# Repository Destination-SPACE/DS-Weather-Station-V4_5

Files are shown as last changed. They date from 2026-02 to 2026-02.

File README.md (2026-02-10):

<div align="center">
    
    <h1>Destination Weather Station v4.5.2</h1>
    <p>An Open Source Remote Sensing Platform for National Taiwan Normal University 🇹🇼</p>
</div>

## 🌟 About the Project
Destination Weather Station is the the latest version of remote sensing tools developed to teach students across Taiwan about climate science and remote sensing in partnership with National Taiwan Normal University.
## ⚙️ Hardware
All hardware files can be found [here](hardware/destinationWeatherStation_v4-5/)
## 💻 Software
All program files can be found [here](software)
## 🗂️ Documentation
Documentation for the weather station can be found [here](https://destination-space.github.io/DS-Weather-Station-V4_5/)
## Licenses
Each of the above sections are individually licensed. Terms and conditions apply within their respective folders.

**Documentation - [Apache License 2.0](docs/LICENSE)** <br>
**Hardware - [CERN-OHL-P](hardware/destinationWeatherStation_v4-5//LICENSE)** <br>
**Software - [The MIT License](software/LICENSE)**

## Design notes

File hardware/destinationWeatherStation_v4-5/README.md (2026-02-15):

# Destination Weather Station v4.5 Hardware
KiCad files for Destination Weather Station v4.5

## KiCanvas
View schematic and PCB files with [KiCanvas](https://kicanvas.org/?github=https%3A%2F%2Fgithub.com%2FDestination-SPACE%2FDS-Weather-Station-V4_5%2Ftree%2Fmain%2Fhardware%2FdestinationWeatherStation_v4-5)

## Directory
### [🧾 Bill of Materials](bom/bom.md)
### [📐 Gerbers](manufacturing/gerbers)
### [📰 Schematics](manufacturing/destinationWeatherStation_v4-5.pdf)

Licensed under [CERN-OHL-P](LICENSE)

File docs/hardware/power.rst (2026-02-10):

.. Copyright 2026 Destination SPACE Inc.
   Licensed under the Apache License, Version 2.0 (the "License");
   you may not use this file except in compliance with the License.
   You may obtain a copy of the License at

      http://www.apache.org/licenses/LICENSE-2.0

   Unless required by applicable law or agreed to in writing, software
   distributed under the License is distributed on an "AS IS" BASIS,
   WITHOUT WARRANTIES OR CONDITIONS OF ANY KIND, either express or implied.
   See the License for the specific language governing permissions and
   limitations under the License.

.. _power:

Power
=====

The power subsystem of the weather station was designed with reverse voltage protection in mind. Typically, if a battery is connected to a circuit backwards, it will not work, or worse, fry the entire system. This is why reverse current protection is often added to circuits to prevent such user error. This allows the user to not have to worry about the polarity of their LiPo battery. On the Destination Weather Station v4.5 we have taken this one step further, by not only having reverse voltage/polarity protection, but also correcting this polarity. This works using the same principal as an `AC rectifier <https://en.wikipedia.org/wiki/Rectifier>`_ circuit. This DC rectifier consists of two `N-Channel MOSFETs <https://en.wikipedia.org/wiki/NMOS_logic>`_ and two `P-Channel MOSFETs <https://en.wikipedia.org/wiki/PMOS_logic>`_. These MOSFETs combine to essentially create a rectifier circuit, which will only allow the correct polarity to pass through the FETs. A schematic of this circuit can be found below.



**Note:** There is no over-current protection, so make sure to not exceed 5V in.

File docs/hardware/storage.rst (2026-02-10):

.. Copyright 2026 Destination SPACE Inc.
   Licensed under the Apache License, Version 2.0 (the "License");
   you may not use this file except in compliance with the License.
   You may obtain a copy of the License at

      http://www.apache.org/licenses/LICENSE-2.0

   Unless required by applicable law or agreed to in writing, software
   distributed under the License is distributed on an "AS IS" BASIS,
   WITHOUT WARRANTIES OR CONDITIONS OF ANY KIND, either express or implied.
   See the License for the specific language governing permissions and
   limitations under the License.

.. _storage:

Storage
=======

The storage on the Destination Weather station is simply a microSD card slot to store recorded sensor data for further evalulation. There is also chip-detect functionality which allows the code to know if a card has been inserted or not.

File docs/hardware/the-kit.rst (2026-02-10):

.. Copyright 2026 Destination SPACE Inc.
   Licensed under the Apache License, Version 2.0 (the "License");
   you may not use this file except in compliance with the License.
   You may obtain a copy of the License at

      http://www.apache.org/licenses/LICENSE-2.0

   Unless required by applicable law or agreed to in writing, software
   distributed under the License is distributed on an "AS IS" BASIS,
   WITHOUT WARRANTIES OR CONDITIONS OF ANY KIND, either express or implied.
   See the License for the specific language governing permissions and
   limitations under the License.

.. _the-kit:

What is in the Kit?
===================

.. Insert kit image here

Kit Contents
------------
- Destination Weather Station v4.5.2
- Seeeduino XIAO RP2040 microcontroller w/ headers
- 128x64px OLED display w/ headers
- SPDT power switch
- AAA battery case
- 8GB micro-SD card
- USB-A to USB-C cable
- USB microSD card adapter

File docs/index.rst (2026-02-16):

.. Copyright 2026 Destination SPACE Inc.
   Licensed under the Apache License, Version 2.0 (the "License");
   you may not use this file except in compliance with the License.
   You may obtain a copy of the License at

      http://www.apache.org/licenses/LICENSE-2.0

   Unless required by applicable law or agreed to in writing, software
   distributed under the License is distributed on an "AS IS" BASIS,
   WITHOUT WARRANTIES OR CONDITIONS OF ANY KIND, either express or implied.
   See the License for the specific language governing permissions and
   limitations under the License.

Destination Weather Station v4.5
================================

An Open Source Remote Sensing Platform for National Taiwan Normal University

Contents
--------



.. toctree::
   :caption: Getting Started
   :maxdepth: 2

   hardware/the-kit
   hardware/assembly

.. toctree::
   :caption: Configuration
   :maxdepth: 2

   software/install-arduino-ide

.. toctree::
   :caption: Sensors
   :maxdepth: 2

   sensors/index
   sensors/bme280
   sensors/ens160
   sensors/ltr390
   sensors/scd40
   sensors/veml7700

.. toctree::
   :caption: Hardware
   :maxdepth: 2

   hardware/index
   faq/troubleshooting
   hardware/power
   hardware/storage
   hardware/hid

.. toctree::
   :caption: Software
   :maxdepth: 2

   software/index
   software/blink
   software/sensor-test
   software/demo
   software/full-code

.. toctree::
   :caption: Activities
   :maxdepth: 2

   activities/index
   activities/temperature
   activities/humidity
   activities/CO2
   activities/VOCs
   activities/ALS
   activities/UVA

.. toctree::
   :caption: Manufacturing and Ordering Kits
   :maxdepth: 1

   manufacturing/index
   manufacturing/pcbs
   manufacturing/adafruit_sensors
   manufacturing/3d_printing
   manufacturing/building_kits

.. toctree::
   :caption: Miscellaneous
   :maxdepth: 2

   FAQ <faq/index>

.. * :ref:`genindex`
.. * :ref:`modindex`
.. * :ref:`search`

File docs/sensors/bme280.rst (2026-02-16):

.. Copyright 2026 Destination SPACE Inc.
   Licensed under the Apache License, Version 2.0 (the "License");
   you may not use this file except in compliance with the License.
   You may obtain a copy of the License at

      http://www.apache.org/licenses/LICENSE-2.0

   Unless required by applicable law or agreed to in writing, software
   distributed under the License is distributed on an "AS IS" BASIS,
   WITHOUT WARRANTIES OR CONDITIONS OF ANY KIND, either express or implied.
   See the License for the specific language governing permissions and
   limitations under the License.

.. _bme280:

BME280
======



The BME280 combined humidity and pressure sensor is a classic device used for accurately measuring temperature, pressure, and humidity.

Humidity
~~~~~~~~

.. list-table::
   :header-rows: 1

   * - Parameter
     - Specifications

   * - Operating Range
     - 0 - 100 %RH
   
   * - Absolute Accuracy
     - ±3 %RH
   
   * - Hysteresis
     - ± %RH



Pressure
~~~~~~~~

.. list-table::
   :header-rows: 1

   * - Parameter
     - Specifications

   * - Operating Range
     - 0 - 1100 hPa

   * - Absolute Accuracy
     - ± 1.0 hPa

   * - Relative Accuracy (700 - 900 hPa & 25 - 40 °C)
     - ± 0.12 hPa

Temperature
~~~~~~~~~~~

.. list-table::
   :header-rows: 1

   * - Parameter
     - Specifications

   * - Operating Range
     - 0 - 65 °C
   
   * - Absolute Accuracy
     - 0.5 °C

Functional Block Diagram
~~~~~~~~~~~~~~~~~~~~~~~~
Below is a functional block diagram for how the BME280 sensor works. The data for each parameter (humidity, pressure, and temperature) are measured using an analog sensor. The data is then converted from an analog voltage signal to a digital data signal. This data is then passed to the logic side of the sensor which sends and receives data to/from the host device.



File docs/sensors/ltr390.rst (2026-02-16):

.. Copyright 2026 Destination SPACE Inc.
   Licensed under the Apache License, Version 2.0 (the "License");
   you may not use this file except in compliance with the License.
   You may obtain a copy of the License at

      http://www.apache.org/licenses/LICENSE-2.0

   Unless required by applicable law or agreed to in writing, software
   distributed under the License is distributed on an "AS IS" BASIS,
   WITHOUT WARRANTIES OR CONDITIONS OF ANY KIND, either express or implied.
   See the License for the specific language governing permissions and
   limitations under the License.

.. _ltr390:

LTR390
======



The LTR390 optical sensor is a combined digital ambient light (ALS) and UVA sensor.

Ambient Light Specifications
~~~~~~~~~~~~~~~~~~~~~~~~~~~~

.. list-table::
   :header-rows: 1

   * - Parameter
     - Minimum
     - Typical
     - Maximum
     - Units
     - Condition
   
   * - ALS Output Resolution
     - 13
     - 18
     - 20
     - Bit
     - Programmable for 13, 16, 17, 18, 19, 20 bit
   
   * - Dark Level Count
     - -
     - 0
     - 5
     - count
     - 0 Lux, T_ope=25°C, 18-bit range

   * - Calibrated Lux Error In Gain Range 3
     - -10
     - -
     - 10
     - %
     - While LED, 5000K, T_ope=25°C

   * - ALS Accuracy
     - -25
     - -
     - 25
     - %
     - Across different light sources

UVS Specifications
~~~~~~~~~~~~~~~~~~

.. list-table::
   :header-rows: 1

   * - Parameter
     - Minimum
     - Typical
     - Maximum
     - Unit
     - Condition

   * - UVS Output Resolution
     - 13
     - 18
     - 20
     - Bit
     - Programmable for 13, 16,17, 18, 19, 20 bit
   
   * - UV Count
     - -
     - 160
     - -
     - count
     - UV LED 310nm, T_ope=25°C, 18-bit, Gain range = 18, Irradiance = 70uW/cm2

   * - UV Sensitivity
     - -
     - 2300
     - -
     - Counts/UVI
     - Gain range = 18, 20-bit

   * - UVI Accuracy (UVI>5)
     - -20
     - -
     - 20
     - %
     - Gain Range = 18, 20bit

   * - UVI Accuracy (UVI<5)
     - -1
     - -
     - 1
     - %
     - Gain Range = 18, 20bit

ALS Sensor
~~~~~~~~~~

The ambient light sensor is sensitive to a range of 450nm - 650nm and is centered at 535nm as seen in the graph below.



Additionally, below is a graph showing the angle of incidence of the sensor, where a normalized count of 1 indicates full sensitivity.



UVS Sensor
~~~~~~~~~~

The UVS sensor peaks in sensitive for UVA wavelengths (315-400) with some moderate sensitivity to low-energy UVB wavelengths. The graph below indicates the the response of the UVS sensor, which has a range of 275nm - 400nm and is centered at 320nm.



The Ultra-Violet Spectrum
~~~~~~~~~~~~~~~~~~~~~~~~~
The ultra-violet spectrum ranges from 10nm to 400nm. This is further subdivided into different bands of intensity, which are used in remote sensing and to indicate their danger.



UVA
~~~

UVA is the longest wavelength of the UV spectrum, ranging from 400nm to 315nm. UVA is the primary cause of sunburns encountered from being in the sun too long. This is because the longer wavelength allows it to penetrate deeper into the skin.

UVB
~~~

UVB is a the middle band of the UV spectrum and ranges from 315nm to 280nm. UVB is mostly absorbed by the ozone layer, but can still reach the earth's surface. This is primarily seen at higher latitudes and elevations. Because UVB has a shorter wavelength, this is the primary cause of skin cancer and blistering from sunburns.

UVC
~~~

UVB is the highest energy band in the UV spectrum, ranging from 280nm to 100nm. UVC is entirely filtered out by the Earth's atmosphere, so is no danger to life on the surface, but can become a risk during air travel or in space. UVC is a type of ionizing radiation, meaning it easily kills cells. This is useful for UV disinfection lights.

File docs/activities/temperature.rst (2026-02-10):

.. Copyright 2026 Destination SPACE Inc.
   Licensed under the Apache License, Version 2.0 (the "License");
   you may not use this file except in compliance with the License.
   You may obtain a copy of the License at

      http://www.apache.org/licenses/LICENSE-2.0

   Unless required by applicable law or agreed to in writing, software
   distributed under the License is distributed on an "AS IS" BASIS,
   WITHOUT WARRANTIES OR CONDITIONS OF ANY KIND, either express or implied.
   See the License for the specific language governing permissions and
   limitations under the License.

.. _temperature:

Temperature Activity - Microclimates
====================================

Duration: 15 minutes

Background
----------

Materials
---------

- Destination Weather Station
- Paper
- Pencil

Procedure
---------

1. Make a map of the classroom on a sheet of paper. Make sure to label any windows, doors, air vents, and significant heat sources.
2. Make a prediction for which areas of the classroom you think will be hot or cold.
3. On your map, mark locations in the classroom you want to collect data.
4. Using your weather station, record the average temperature at each location you marked on your map.

Discussion Questions
--------------------

1. Did your predictions match the data you collected? Why might they be different?
2. What do you think caused that part of the classroom to be that temperature?

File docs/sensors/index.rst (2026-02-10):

.. Copyright 2026 Destination SPACE Inc.
   Licensed under the Apache License, Version 2.0 (the "License");
   you may not use this file except in compliance with the License.
   You may obtain a copy of the License at

      http://www.apache.org/licenses/LICENSE-2.0

   Unless required by applicable law or agreed to in writing, software
   distributed under the License is distributed on an "AS IS" BASIS,
   WITHOUT WARRANTIES OR CONDITIONS OF ANY KIND, either express or implied.
   See the License for the specific language governing permissions and
   limitations under the License.

.. _sensors:

Overview of Sensors
===================

The Destination Weather Station is equipped with a :ref:`Bosch BME280 combined humidity and pressure sensor<bme280>`.

In the expansion sensor kit, several more environmental sensors are provided to measure a wide variety of parameters. These include:

* :ref:`ScioSense ENS160 - Digital metal-oxide multi-gas sensor<ens160>`
* :ref:`Lite-On LTR390 - Ambient light and ultravoiolet light sensor<ltr390>`
* :ref:`Sensirion SCD40 - Miniature CO2 sensor<SCD40>`
* :ref:`Vishay VEML7700 - High accuracy ambient light sensor<veml7700>`

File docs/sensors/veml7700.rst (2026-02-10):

.. Copyright 2026 Destination SPACE Inc.
   Licensed under the Apache License, Version 2.0 (the "License");
   you may not use this file except in compliance with the License.
   You may obtain a copy of the License at

      http://www.apache.org/licenses/LICENSE-2.0

   Unless required by applicable law or agreed to in writing, software
   distributed under the License is distributed on an "AS IS" BASIS,
   WITHOUT WARRANTIES OR CONDITIONS OF ANY KIND, either express or implied.
   See the License for the specific language governing permissions and
   limitations under the License.

.. _veml7700:

VEML7700
========



The VEML7700 high accuracy 16-bit light sensor can be used to precisely measure ambient light. Below is a functional block diagram of the device, where the sensor is an ALS photodiode.



Specifications
~~~~~~~~~~~~~~

.. list-table::
   :header-rows: 1

   * - Parameter
     - Typical Value
     - Units
   
   * - Digital resolution
     - 0.0036
     - lux/bit
   
   * - Detectable minimum illuminance
     - 0.0072
     - lux
   
   * - Detectable maximum illuminance
     - 120,000
     - lux
   
   * - Dark offset
     - 3
     - steps

Below is a graph showing the spectral response of the sensor. It is sensitive to wavelengths ranging from 450nm - 650nm, normalized at 550nm.



Additionally, below is a graph showing the sensitivity of the white light channel on the sensor.



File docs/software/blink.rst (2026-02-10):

.. Copyright 2026 Destination SPACE Inc.
   Licensed under the Apache License, Version 2.0 (the "License");
   you may not use this file except in compliance with the License.
   You may obtain a copy of the License at

      http://www.apache.org/licenses/LICENSE-2.0

   Unless required by applicable law or agreed to in writing, software
   distributed under the License is distributed on an "AS IS" BASIS,
   WITHOUT WARRANTIES OR CONDITIONS OF ANY KIND, either express or implied.
   See the License for the specific language governing permissions and
   limitations under the License.

.. _blink-sketch:

Blink Sketch
============

The `Blink <https://github.com/Destination-SPACE/DS-Weather-Station-V4_5/blob/main/software/Blink/Blink.ino>`_ sketch is used as a beginners program and to test the on-board RGB LED and NeoPixel.

Libraries
---------

The Blink Sketch has only one required library. This library is the `Adafruit NeoPixel Library <https://github.com/adafruit/Adafruit_NeoPixel>`_. This is used to send commands to the NeoPixel RGB LED on the Seeeduino XIAO.

.. code-block:: cpp
   
   #include <Adafruit_NeoPixel.h>

Hardware Definitions
--------------------

Several hardware definitions need to be defined to use the RBG LED and the NeoPixel. These are defined by assigning each variable a General Purpose Input-Output (GPIO) pin on the XIAO and any other criteria specified by the NeoPixel library. What these definitions do is define the red, green, and blue pins of the normal RGB LED a GPIO pin, define the power and signal pin for the NeoPixel, and define the number of NeoPixels on the board.

.. code-block:: cpp

   #define RGB_R 17
   #define RGB_G 16
   #define RGB_B 25
   #define NEOPIXEL_PWR 11
   #define NEOPIXEL_PIN 12
   #define NEOPIXEL_NUM 1

Following the hardware definitions, the information specified above needs to be defined in the NeoPixel definition function

.. code-block:: cpp

   Adafruit_NeoPixel pixels(NEOPIXEL_NUM, NEOPIXEL_PIN, NEO_GRB + NEO_KHZ800);

Setup Function
--------------

The next step is to initialize the LEDs for the primary loop function. This is done by starting the NeoPixel function, initializing the power and signal pins, and defining the RGB LEDs pins as outputs.

.. code-block:: cpp

   void setup() {
      //Initialize NeoPixel
      pixels.begin();
      pinMode(NEOPIXEL_PWR, OUTPUT);
      digitalWrite(NEOPIXEL_PWR, HIGH);

      //Initialize RGB LED
      pinMode(RGB_R, OUTPUT);
      pinMode(RGB_G, OUTPUT);
      pinMode(RGB_B, OUTPUT);
   }

Loop Function
-------------

The final step is to send the commands to the NeoPixel and RGB LED. This is done by first clearing the NeoPixel's stored data, defining the color, and sending the neopixel the data. Additionally, there is a custom function to easily control the color of the RGB LED. This works by passing the red, green, and blue values to the function ``setColor()``. An example of the NeoPixel code and the RGB LED can be found below

.. code-block:: cpp
   
   pixels.clear();
   pixels.setPixelColor(0, pixels.Color(15, 25, 205));
   delay(400); // How long the NeoPixel stays on
   pixels.show();

.. code-block:: cpp
   
   setColor(15, 25, 205);

   void setColor(int VAL_GRN, int VAL_RED, int VAL_BLU){
      analogWrite(RGB_R, 255 - VAL_RED);
      analogWrite(RGB_G, 255 - VAL_GRN);
      analogWrite(RGB_B, 255 - VAL_BLU);
   }

Full Code
--------- 

Below is the full Blink example sketch

.. code-block:: cpp
   
   #include <Adafruit_NeoPixel.h> // Import Adafruit NeoPixel library

   //Define Hardware
   #define RGB_R 17
   #define RGB_G 16
   #define RGB_B 25
   #define NEOPIXEL_PWR 11
   #define NEOPIXEL_PIN 12
   #define NEOPIXEL_NUM 1

   Adafruit_NeoPixel pixels(NEOPIXEL_NUM, NEOPIXEL_PIN, NEO_GRB + NEO_KHZ800); // Define NeoPixel

   void setup() {
      //Initialize NeoPixel
      pixels.begin();
      pinMode(NEOPIXEL_PWR, OUTPUT);
      digitalWrite(NEOPIXEL_PWR, HIGH);

      //Initialize RGB LED
      pinMode(RGB_R, OUTPUT);
      pinMode(RGB_G, OUTPUT);
      pinMode(RGB_B, OUTPUT);
   }

   void loop() { 
      pixels.clear();
      pixels.setPixelColor(0, pixels.Color(15, 25, 205));
      setColor(15, 25, 205);
      delay(400);

      pixels.show();
      pixels.clear();
      pixels.setPixelColor(0, pixels.Color(103, 25, 205));
      setColor(15, 25, 205);
      delay(400);

      pixels.show();
      pixels.clear();
      pixels.setPixelColor(0, pixels.Color(233, 242, 205));
      setColor(233, 242, 205);
      delay(400);

      pixels.show();
      pixels.clear();
      pixels.setPixelColor(0, pixels.Color(233, 23, 23));
      setColor(233, 23, 23);
      delay(400);

      pixels.show();
      pixels.clear();
      pixels.setPixelColor(0, pixels.Color(12, 66, 101));
      setColor(12, 66, 101);
      delay(400);

      pixels.show();
      delay(500);
   }

   //Function to change color of RGB LED
   void setColor(int VAL_GRN, int VAL_RED, int VAL_BLU){
      analogWrite(RGB_R, 255 - VAL_RED);
      analogWrite(RGB_G, 255 - VAL_GRN);
      analogWrite(RGB_B, 255 - VAL_BLU);
   }

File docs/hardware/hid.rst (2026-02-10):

.. Copyright 2026 Destination SPACE Inc.
   Licensed under the Apache License, Version 2.0 (the "License");
   you may not use this file except in compliance with the License.
   You may obtain a copy of the License at

      http://www.apache.org/licenses/LICENSE-2.0

   Unless required by applicable law or agreed to in writing, software
   distributed under the License is distributed on an "AS IS" BASIS,
   WITHOUT WARRANTIES OR CONDITIONS OF ANY KIND, either express or implied.
   See the License for the specific language governing permissions and
   limitations under the License.

.. _hid:

Human Interface Devices
=======================

On the Destination Weather Station there are 4 buttons, which are the primary way to interact with the device. These buttons are each labeled with arrows ↑, ↓, ←, →. These buttons are used to scroll through the menus and to switch between the different data displays.

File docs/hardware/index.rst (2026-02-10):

.. Copyright 2026 Destination SPACE Inc.
   Licensed under the Apache License, Version 2.0 (the "License");
   you may not use this file except in compliance with the License.
   You may obtain a copy of the License at

      http://www.apache.org/licenses/LICENSE-2.0

   Unless required by applicable law or agreed to in writing, software
   distributed under the License is distributed on an "AS IS" BASIS,
   WITHOUT WARRANTIES OR CONDITIONS OF ANY KIND, either express or implied.
   See the License for the specific language governing permissions and
   limitations under the License.

.. _hardware:

Overview of Hardware
====================

The Destination Weather Station was designed in `KiCad <https://www.kicad.org/>`_ and assembled by hand. the weather station includes several features that improve user experience. These are:

.. toctree::
   :maxdepth: 1

   power
   storage
   hid

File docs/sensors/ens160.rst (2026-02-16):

.. Copyright 2026 Destination SPACE Inc.
   Licensed under the Apache License, Version 2.0 (the "License");
   you may not use this file except in compliance with the License.
   You may obtain a copy of the License at

      http://www.apache.org/licenses/LICENSE-2.0

   Unless required by applicable law or agreed to in writing, software
   distributed under the License is distributed on an "AS IS" BASIS,
   WITHOUT WARRANTIES OR CONDITIONS OF ANY KIND, either express or implied.
   See the License for the specific language governing permissions and
   limitations under the License.

.. _ens160:

ENS160
======



The ENS160 digital metal-oxide multi-gas sensor measures volatile organic compounds (VOCs), which can be used to measure total VOC content (TVOC), air quality index (AQI), and calculate an approximate value for carbon-dioxide concentration (eCO2).

Specifications
~~~~~~~~~~~~~~

.. list-table::
   :header-rows: 1

   * - Parameter
     - Range
     - Resolution
     - Units

   * - TVOC
     - 0 - 65,000
     - 1
     - ppb

   * - eCO2
     - 400 - 65,000
     - 1
     - ppm CO2 equivalent

   * - AQI-UBA
     - 1 to 5
     - 1
     - -

   * - AQI-EPA
     - 0 - 500
     - 1
     - -

TVOC
~~~~
Total Volatile Organic Compounds (TVOC) is a useful parameter used to determine the quality of the air in a given area. This is incredibly important for urban environments and in indoor settings. This is typically measured in parts-per-billion (ppb), but in polluted environments, can reach into the parts-per-million (ppm) range.

eCO2
~~~~
The ENS160 sensor uses an algorithm to calculate an approximate value for carbon-dioxide (CO2) concentration. While the sensor cannot directly measure CO2, it's algorithm can closely approximate this value, as seen in the graph below.



In the graph, the calculated eCO2 measurement is being compared to a non-dispersive infrared CO2 sensor. It can closely approximate the CO2 concentration, but it is not perfect.

In the graphs below, ScioSense has provided eCO2 measurement for different environments, such as in a bedroom, kitchen, and bathroom. These graphs show that different conditions, such as closing a window, cooking, or being in a room can increase CO2 concentrations.







AQI
~~~
Air Quality Index (AQI) is the typical parameter used to judge the quality of air and how polluted it is. There are several different scales used to measure this value, but they are all based on the concentration of VOCs. For example, the United States uses the `NowCast <https://www.airnow.gov/aqi/aqi-basics/>`_ algorithm developed by the Environmental Protection Agency (EPA) ranging from 0 to 500, the European Union's `European Environment Agency <https://airindex.eea.europa.eu/AQI/index.html>`_ (EEA) uses a scale ranging from 0 to 1250, and Taiwan's `Ministry of Environment <https://airtw.epa.gov.tw/ENG/Information/Standard/AirQualityIndicator.aspx>`_ uses a similar scale to the United States, ranging from 0 to 500. The figures below show each of these indexes.

Environmental Protection Agency (EPA)



European Environment Agency (EEA)



Ministry of Environment



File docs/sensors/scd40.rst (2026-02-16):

.. Copyright 2026 Destination SPACE Inc.
   Licensed under the Apache License, Version 2.0 (the "License");
   you may not use this file except in compliance with the License.
   You may obtain a copy of the License at

      http://www.apache.org/licenses/LICENSE-2.0

   Unless required by applicable law or agreed to in writing, software
   distributed under the License is distributed on an "AS IS" BASIS,
   WITHOUT WARRANTIES OR CONDITIONS OF ANY KIND, either express or implied.
   See the License for the specific language governing permissions and
   limitations under the License.

.. _scd40:

SCD40
=====



THe SCD40 CO2 sensor uses photoacoustic non-dispersive infrared (NDIR) technology to measure actual CO2 concentration, unlike the eCO2 measurement on the :ref:`ENS160<ens160>`. This works by measuring the attenuation of an infrared light shining through the gas onto an acoustic transducer. Along with the sample chamber there is a reference nitrogen sample used to compare the CO2 measurement to the known gas. This process works according to Beer-Lambert law which is this attenuation of the gas.



CO2 Sensing Performance
~~~~~~~~~~~~~~~~~~~~~~~

.. list-table::
   :header-rows: 1

   * - Parameter
     - Conditions
     - Value
   
   * - Output range
     - -
     - 0 - 40,000ppm
   
   * - Accuracy
     - 400ppm - 2,000ppm
     - ±(50ppm + 5% of reading)
   
   * - Repeatability
     - Typical
     - ±10ppm

Humidity Sensing Performance
~~~~~~~~~~~~~~~~~~~~~~~~~~~~

.. list-table::
   :header-rows: 1

   * - Parameter
     - Conditions
     - Value
   
   * - Range
     - -
     - 0 %RH - 100 %RH

   * - Accuracy
     - 15°C - 35°C, 20 %RH - 65 %RH
     - ±6 %RH

   * - Accuracy
     - -10°C - 60°C, 0 %RH - 100 %RH
     - ±9 %RH

   * - Repeatability
     - Typical
     - ±0.4 %RH

Temperature Sensing Performance
~~~~~~~~~~~~~~~~~~~~~~~~~~~~~~~

.. list-table::
   :header-rows: 1

   * - Parameter
     - Conditions
     - Value
   
   * - Range
     - -
     - -10°C - 60°C
   
   * - Accuracy
     - 15°C - 35°C
     - ±0.8°C
   
   * - Accuracy
     - -10°C - 60°C
     - ±1.5°C

   * - Repeatability
     - Typical
     - ±0.1°C

Measuring CO2
~~~~~~~~~~~~~

Measuring CO2 is another important parameter for indoor and outdoor air quality. Health Canada recommends not exceeding 1000ppm of CO2 in a 24 hour period. A high concentration of CO2 can increase the risk of respiratory symptoms, decreased cognitive function, and neurophysiological symptoms such as headaches, tiredness, and dizziness. The graph below shows different concentrations and what effects one may encounter at that concentration.



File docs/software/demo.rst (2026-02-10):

.. Copyright 2026 Destination SPACE Inc.
   Licensed under the Apache License, Version 2.0 (the "License");
   you may not use this file except in compliance with the License.
   You may obtain a copy of the License at

      http://www.apache.org/licenses/LICENSE-2.0

   Unless required by applicable law or agreed to in writing, software
   distributed under the License is distributed on an "AS IS" BASIS,
   WITHOUT WARRANTIES OR CONDITIONS OF ANY KIND, either express or implied.
   See the License for the specific language governing permissions and
   limitations under the License.

.. _demo-sketch:

Demo Sketch
===========

The `Demo <https://github.com/Destination-SPACE/DS-Weather-Station-V4_5/blob/main/software/Demo/Demo.ino>`_ sketch is used as an introductory program to most of the features on the weather station. This includes scrollable menus for all sensors.

There is no data recording in this example.

Button Menu
-----------

On the weather station there are 4 buttons, ↑, ↓, ←, →.

The ← and → buttons are used to scroll between the weather menu, air quality menu, and the light menu.

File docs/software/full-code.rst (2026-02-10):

.. Copyright 2026 Destination SPACE Inc.
   Licensed under the Apache License, Version 2.0 (the "License");
   you may not use this file except in compliance with the License.
   You may obtain a copy of the License at

      http://www.apache.org/licenses/LICENSE-2.0

   Unless required by applicable law or agreed to in writing, software
   distributed under the License is distributed on an "AS IS" BASIS,
   WITHOUT WARRANTIES OR CONDITIONS OF ANY KIND, either express or implied.
   See the License for the specific language governing permissions and
   limitations under the License.

.. _blink:

Full Code Sketch
================

The `Full Code <https://github.com/Destination-SPACE/DS-Weather-Station-V4_5/blob/main/software/Full_Code/Full_Code.ino>`_ sketch incorporates all of the components of the weather station, including data recording. This has all the menus of the `Demo <https://github.com/Destination-SPACE/DS-Weather-Station-V4_5/blob/main/software/Demo/Demo.ino>`_ sketch as well as a menu used to start and stop data recording.

Program Overview
----------------

Button Menu
-----------

On the weather station there are 4 buttons, ↑, ↓, ←, →.

The ← and → buttons are used to scroll between the weather menu, air quality menu, and the light menu.

The ↑ arrow is used to navigate to the data recording menu. Here you can choose to either start recording data or pause data recording. **data recording is paused by default**. Press the → button to confirm your selection.

The ↓ is used to navigate the data recording menu above. When in either the air quality or light menu, pressing it will return you to the weather menu.

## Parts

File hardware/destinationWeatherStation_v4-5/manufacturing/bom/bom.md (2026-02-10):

# Bill of Materials
*Note: Some parts may be replaced with suitable alternatives

| Item | Qty | Reference | Value | Datasheet | Manufacturer | Manufacturer Part Number | Package |
|-----:|----:|:---------:|:-----:|:----------|:-------------|:-------------------------|--------:|
| 1 | 1 | C1 | 10uF | [AVX-CX5R-KGM](../datasheets/AVX-CX5R-KGM-MLCC.pdf) | KYOCERA AVX | KGM15CR51A106MT | 0603 |
| 2 | 3 | C2, C3, C4 | 0.1uF | [AVX-CX5R-KGM](../datasheets/AVX-CX5R-KGM-MLCC.pdf) | KYOCERA AVX | KGM15AR51H104KT | 0603 | 
| 3 | 10 | R1, R2, R3, R4, R5, R6, R7, R8, R9, R10 | 10K | [D/CRCW e3](../datasheets/Vishay-Dale-DCRCWe3.pdf) | Vishay Dale | CRCW060310K0JNEB | 0603 |
| 3 | 2 | R11, R12 | 0R | [D/CRCW e3](../datasheets/Vishay-Dale-DCRCWe3.pdf) | Vishay Dale | CRCW06030000Z0EA | 0603 |
| 4 | 2 | Q1, Q2 | IRLML6244TRPBF | [IRLML6244TRPBF](../datasheets//Infineon-IRLML6244.pdf) | Infineon Technologies | IRLML6244TRPBF | SOT-23 |
| 5 | 2 | Q3, Q4 | DMP2035UVTQ | [DMP2035UVTQ](../datasheets/Diodes-Incorporated-DMP2035UVTQ.pdf) | Diodes Incorporated | DMP2035UVTQ-7 | TSOT26 |
| 6 | 1 | U1 | XIAO RP2040 | [XIAO RP2040](https://wiki.seeedstudio.com/XIAO-RP2040/) | Seeed Studio | XIAO RP2040 | N/A |
| 7 | 1 | U2 | BME280 | [BME280](../datasheets/BST-BME280.pdf) | Bosch Sensortec | BME280 | 2.5x2.5mm LGA |
| 8 | 1 | U3 | OLED | [HS96L03W2C03](../datasheets/HS-HS96L03W2C03.pdf) | SHENZHEN HANSHENG INDUSTRAIL CO. | HS96L03W2C03 | N/A |
| 9 | 1 | SW1 | OS102011MS2QN1 | [OS102011MS2QN1](https://www.ckswitches.com/media/1428/os.pdf) | C&K | OS102011MS2QN1 | N/A |
| 10 | 4 | SW2, SW3, SW4, SW5 | PTS647SM38SMTR2LFS | [PTS647SM38SMTR2LFS](../datasheets/C&K-PTS647.pdf) | C&K | PTS 647 SM38 SMTR2 LFS | N/A |
| 11 | 1 | J1 | S2B-PH-SM4 | [JST-PH](../datasheets/JST-PH-Connectors.pdf) | JST Sales America Inc. | S2B-PH-SM4-TB(LF)(SN) | N/A |
| 12 | 1 | J2 | MEM2061 | [MEM2061](../datasheets//GCT-MEM2061.pdf) | GCT | MEM2061-01-188-00-A | N/A |
| 13 | 1 | J3 | SM04B-SRSS | [JST-SH](../datasheets/JST-SH-Connectors.pdf) | JST Sales America Inc. | SM04B-SRSS-TB | N/A |

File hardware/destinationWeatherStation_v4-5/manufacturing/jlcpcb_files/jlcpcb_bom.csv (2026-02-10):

Reference | Qty | Value | Footprint | JLCPCB PN
C1 | 1 | 10uF | lib_fp:CAPC160X80X88L35N | C1691
C2,C3,C4 | 3 | 100nF | lib_fp:CAPC160X80X88L35N | C1590
J1 | 1 | S2B-PH-SM4 | lib_fp:JST-PH-S2B-SM4-TB | C295747
J2 | 1 | MEM2061 | lib_fp:MEM2061 | C5151738
J3 | 1 | STEMMA_QT | lib_fp:JST_SH_SM04B-SRSS-TB | C160404
Q1,Q2 | 2 | IRLML6244TRPBF | lib_fp:IRLML6244TRPBF | C5123965
Q3,Q4 | 2 | DMP2035UVTQ-7 | lib_fp:SOT23-6P95_280X100L40X37N | C5126680
R1,R2,R3,R4,R5,R6,R7,R8,R9,R10 | 10 | 10K | lib_fp:RESC160X80X55L30N | C1511834
R11,R12 | 2 | 0R | lib_fp:ResistorJumper-3 | C844915
SW2,SW3,SW4,SW5 | 4 | PTS647SM38SMTR2LFS | lib_fp:SW_4.5x4.5 | C2689502
U2 | 1 | BME280 | lib_fp:BME280 | C92489

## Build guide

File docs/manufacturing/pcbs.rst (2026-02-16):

.. Copyright 2026 Destination SPACE Inc.
   Licensed under the Apache License, Version 2.0 (the "License");
   you may not use this file except in compliance with the License.
   You may obtain a copy of the License at

      http://www.apache.org/licenses/LICENSE-2.0

   Unless required by applicable law or agreed to in writing, software
   distributed under the License is distributed on an "AS IS" BASIS,
   WITHOUT WARRANTIES OR CONDITIONS OF ANY KIND, either express or implied.
   See the License for the specific language governing permissions and
   limitations under the License.

.. _pcbs:

Manufacturing PCBs
==================

To manufacture the Destination Weather Station v4.5, files for JLCPCB have been provided.

Download Files
--------------

JLCPCB handles the manufacturing and assembly of the weather station PCB.

Download the following files from the GitHub repository.

- `Gerbers <https://github.com/Destination-SPACE/DS-Weather-Station-V4_5/blob/main/hardware/destinationWeatherStation_v4-5/manufacturing/jlcpcb_files/jlcpcb_gerbers.zip>`_
- `Bill of materials <https://github.com/Destination-SPACE/DS-Weather-Station-V4_5/blob/main/hardware/destinationWeatherStation_v4-5/manufacturing/jlcpcb_files/jlcpcb_bom.csv>`_
- `Component placement <https://github.com/Destination-SPACE/DS-Weather-Station-V4_5/blob/main/hardware/destinationWeatherStation_v4-5/manufacturing/jlcpcb_files/jlcpcb_cpl.csv>`_

Ordering
--------

1. Go to `JLCPCB.com/quote <https://cart.jlcpcb.com/quote>`_

2. Click **Add gerber file** and upload the ``jlcpcb_gerbers.zip`` file

3. Change the following parameters

   - PCB Qty: Select a quantity
   - PCB Color: Select any color (this may change cost or manufacturing time)
   - Surface Finish: LeadFree HASL
   - PCB Assembly > PCB Type: Standard

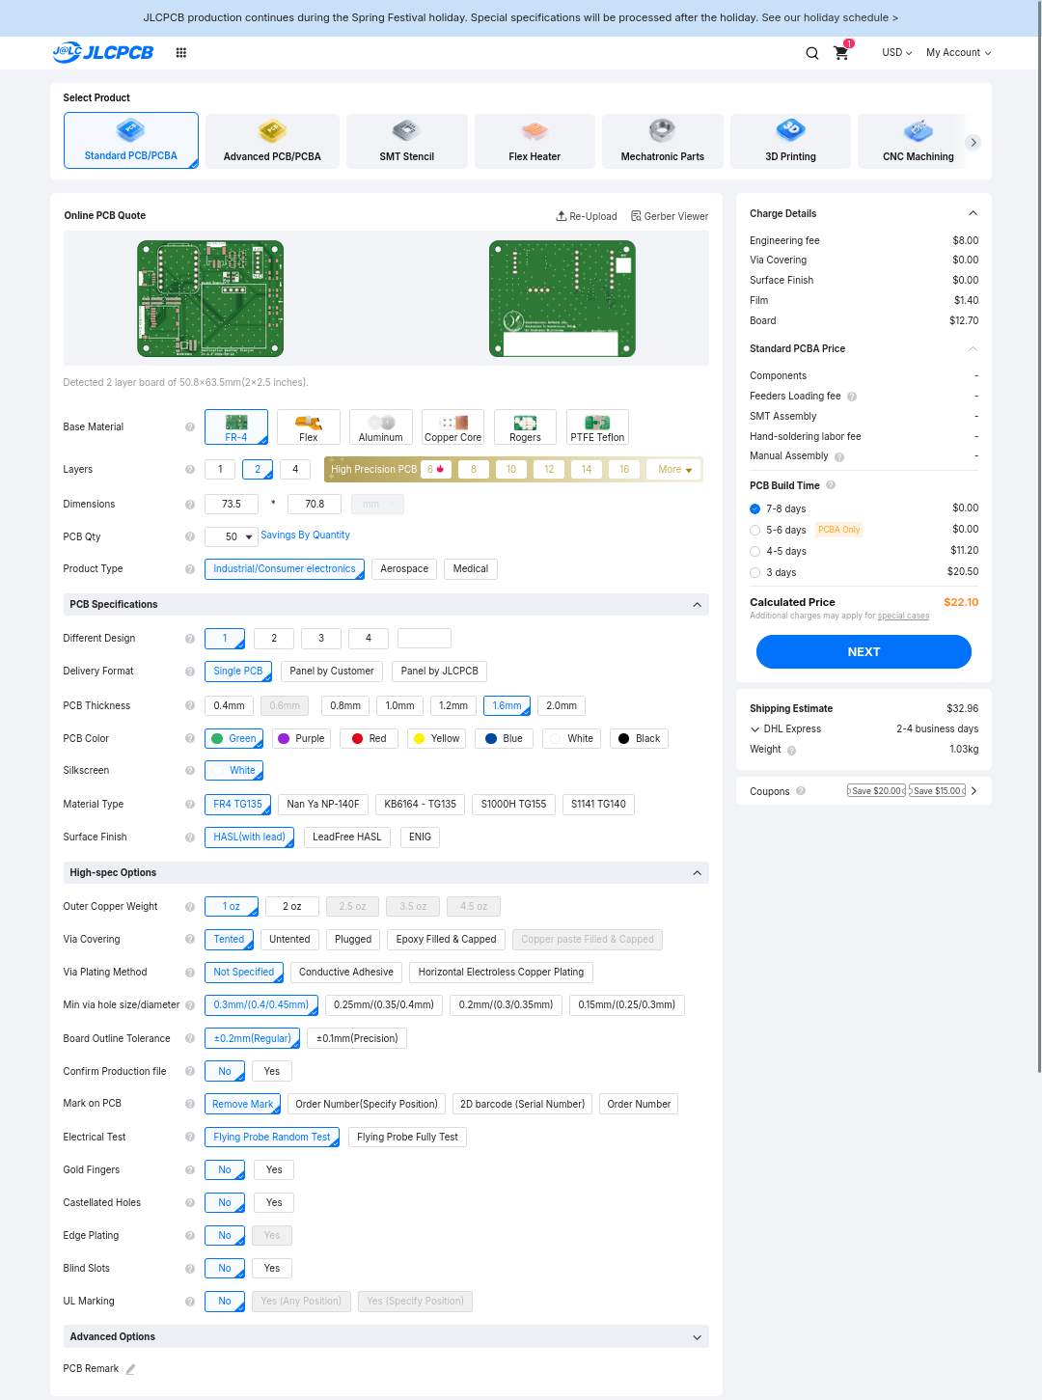
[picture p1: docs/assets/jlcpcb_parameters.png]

      
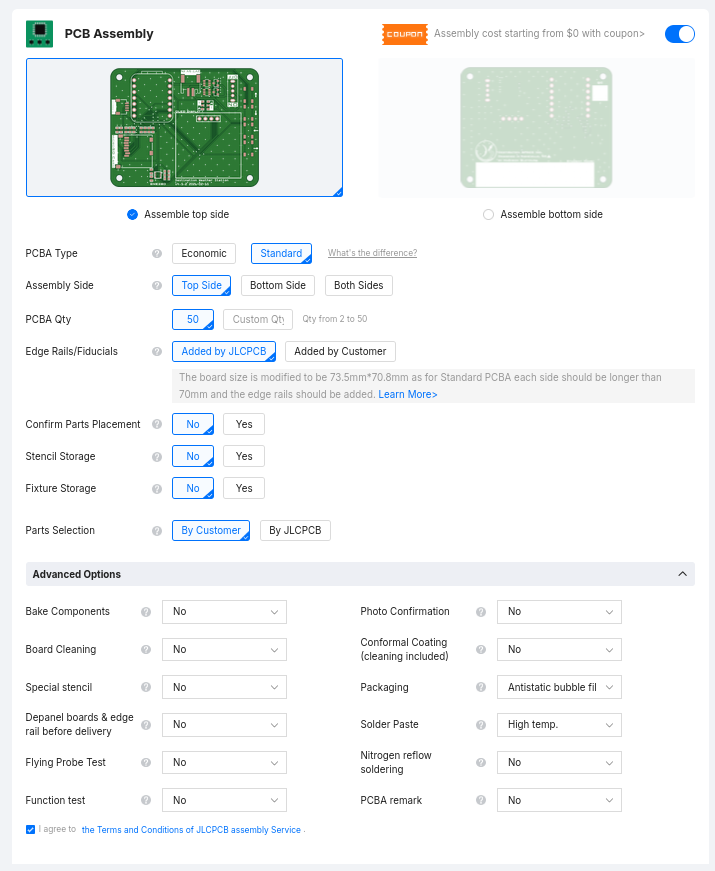
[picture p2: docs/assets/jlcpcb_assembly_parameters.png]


4. Click **Next**

5. Click **Next**

6. Upload the ``jlcpcb_bom.csv`` and ``jlcpcb_cpl.csv`` files.

7. Click **Process BOM & CPL**

8. Click **Next**

   If components are unavailable, make substitutions.

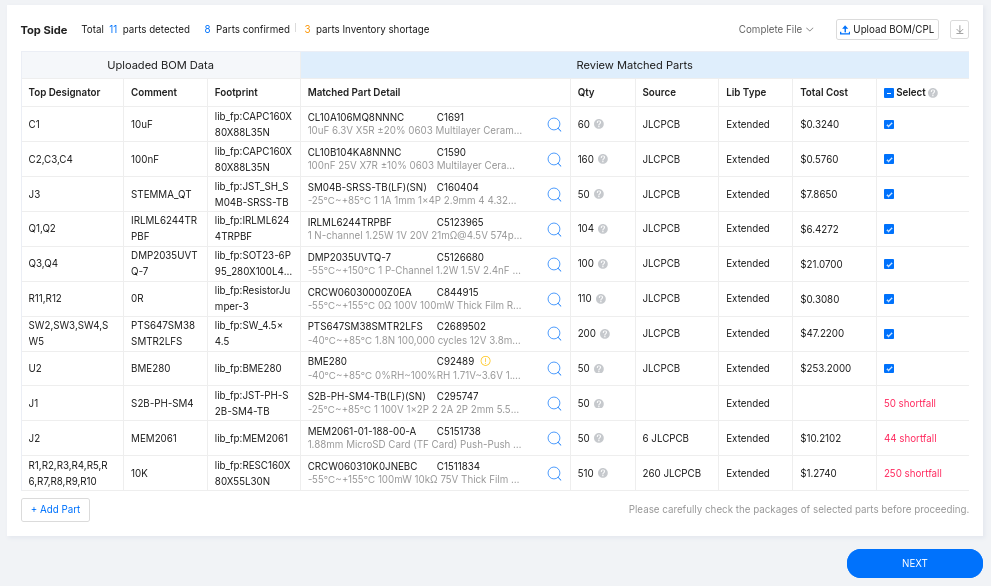
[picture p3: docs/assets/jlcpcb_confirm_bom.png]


9. Click **Next**

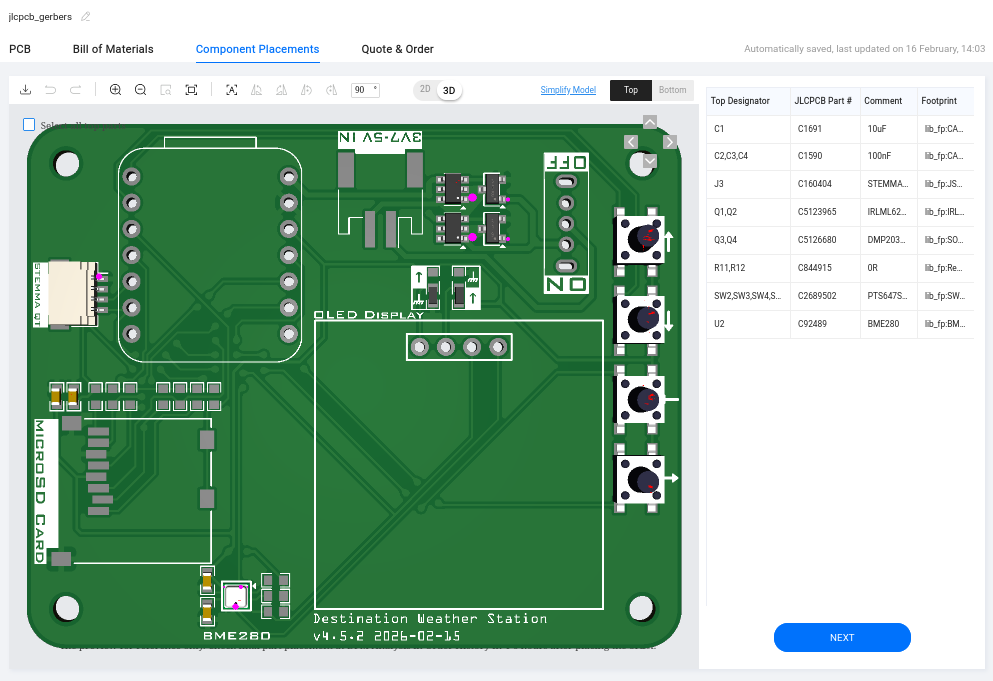
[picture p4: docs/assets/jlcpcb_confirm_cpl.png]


10. If asked, select `Research\Education\DIY\Entertainment > Development Board - HS Code 847330` for the product description.

11. Click **Save to Cart**

12. Complete purchase

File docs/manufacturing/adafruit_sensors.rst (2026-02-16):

.. Copyright 2026 Destination SPACE Inc.
   Licensed under the Apache License, Version 2.0 (the "License");
   you may not use this file except in compliance with the License.
   You may obtain a copy of the License at

      http://www.apache.org/licenses/LICENSE-2.0

   Unless required by applicable law or agreed to in writing, software
   distributed under the License is distributed on an "AS IS" BASIS,
   WITHOUT WARRANTIES OR CONDITIONS OF ANY KIND, either express or implied.
   See the License for the specific language governing permissions and
   limitations under the License.

.. _adafruit_sensors:

Adafruit Expansion Sensors
==========================

Below is a list of the components needed to build a classroom set of environmental sensors

.. list-table::
  :header-rows: 1

  * - Component
    - Manufacturer
    - Manufacturer Part Number
    - Quantity
    - Link

  * - SCD-40 - True CO2 Sensor
    - Adafruit
    - 5187
    - 7
    - `https://www.adafruit.com/product/5187`

  * - ENS160 - MOX Gas Sensor
    - Adafruit
    - 5606
    - 8
    - `https://www.adafruit.com/product/5606`

  * - VEML7700 - Lux Sensor
    - Adafruit
    - 4162
    - 8
    - `https://www.adafruit.com/product/4162`

  * - LTR390 - UV Light Sensor
    - Adafruit
    - 4831
    - 8
    - `https://www.adafruit.com/product/4831`

  * - STEMMA QT JST SH 4-Pin Cable - 50mm
    - Adafruit
    - 4399
    - 24
    - `https://www.adafruit.com/product/4399`

  * - STEMMA QT JST SH 4-Pin Cable - 100mm
    - Adafruit
    - 4210
    - 12
    - `https://www.adafruit.com/product/4210`

  * - Adafruit Swirly Aluminum Mounting Grid - 5x5
    - Adafruit
    - 5779
    - 8
    - `https://www.adafruit.com/product/5779`

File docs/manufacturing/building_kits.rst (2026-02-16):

.. Copyright 2026 Destination SPACE Inc.
   Licensed under the Apache License, Version 2.0 (the "License");
   you may not use this file except in compliance with the License.
   You may obtain a copy of the License at

      http://www.apache.org/licenses/LICENSE-2.0

   Unless required by applicable law or agreed to in writing, software
   distributed under the License is distributed on an "AS IS" BASIS,
   WITHOUT WARRANTIES OR CONDITIONS OF ANY KIND, either express or implied.
   See the License for the specific language governing permissions and
   limitations under the License.

.. _building_kits:

Additional Materials
--------------------

To complete the kit, a few additional components will need to be sourced as these will be soldered by the students. These components can be found in the table below.

.. list-table::
   :header-rows: 1

   * - Component
     - Manufacturer
     - Manufacturer Part Number
     - Link

   * - XIAO RP2040
     - Seeed Studio
     - XIAO RP2040
     - `https://www.seeedstudio.com/XIAO-RP2040-v1-0-p-5026.html`

   * - SPDT slide switch
     - C&K
     - OS102011MS2QN1
     - `https://www.lcsc.com/product-detail/C221829.html`

   * - 128x64 SSD1315 OLED display
     - HS
     - HS96L03W2C03
     - `https://www.lcsc.com/product-detail/C5248080.html`

   * - Pin header 4 position 2.54mm pitch
     - XFCN
     - PZ254V-11-04P
     - `https://www.lcsc.com/product-detail/C2691448.html`

   * - 3x AAA Battery holder
     - MYOUNG
     - BH-AAA-B1AJ022
     - `https://www.lcsc.com/product-detail/C5290194.html`

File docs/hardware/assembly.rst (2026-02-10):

.. Copyright 2026 Destination SPACE Inc.
   Licensed under the Apache License, Version 2.0 (the "License");
   you may not use this file except in compliance with the License.
   You may obtain a copy of the License at

      http://www.apache.org/licenses/LICENSE-2.0

   Unless required by applicable law or agreed to in writing, software
   distributed under the License is distributed on an "AS IS" BASIS,
   WITHOUT WARRANTIES OR CONDITIONS OF ANY KIND, either express or implied.
   See the License for the specific language governing permissions and
   limitations under the License.

.. _assembly:

Destination Weather Station v4.5 Assembly
=========================================



The Destination Weather Station v4.5 is preassembled with the majority of the circuit components.

Before using the weather station, you will need to :ref:`solder<soldering>` the :ref:`XIAO RP2040 microcontroller<xiao-RP2040>`, :ref:`OLED display<oled-display>`, and :ref:`power switch<switch>`. Follow the instructions below to solder your weather station. You can then :ref:`connect the batteries<batteries>` and insert the microSD card.

Soldering
---------

.. _soldering:

To solder the weather station, follow the instructions below. Tools required to complete these steps are:

* Soldering iron
* Solder wire

Power Switch
~~~~~~~~~~~~

.. _switch:



To solder the power switch to the weather station, insert it into the front side of the board. Flip the board over and solder the pins, starting with the two outer ones.

XIAO RP2040
~~~~~~~~~~~

.. _xiao-RP2040:

To solder the XIAO RP2040 to the weather station, begin by inserting the long side of the 1x7 header pins into the weather station board as shown below.



Next, flip the weather station over and solder all 14 pins to the weather station.

Finally, flip the weather station back over and solder the XIAO to the short side of the header pins. After you are done, it should look like the image below.



OLED Display
~~~~~~~~~~~~

.. _oled-display:

To solder the OLED display to the weather station, you will follow similar procedures to the steps above to solder the XIAO.

Begin by inserting the long side of the 1x4 header into the weather station board as shown below.



Next, flip the board over and solder the pins to the back.

Similarly, flip the board back over and solder the display to the front.



Final Assembly
--------------


Batteries
~~~~~~~~~

.. _batteries:

Insert three (3) AAA batteries into the battery pack. Connect the JST-PH connector to the matching connector on the weather station.

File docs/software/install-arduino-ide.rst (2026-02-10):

.. Copyright 2026 Destination SPACE Inc.
   Licensed under the Apache License, Version 2.0 (the "License");
   you may not use this file except in compliance with the License.
   You may obtain a copy of the License at

      http://www.apache.org/licenses/LICENSE-2.0

   Unless required by applicable law or agreed to in writing, software
   distributed under the License is distributed on an "AS IS" BASIS,
   WITHOUT WARRANTIES OR CONDITIONS OF ANY KIND, either express or implied.
   See the License for the specific language governing permissions and
   limitations under the License.

.. _install-arduino-ide:

Installing Arduino IDE
======================

To program the Destination Weather Station, you will need to download and install Arduino IDE.

Download
~~~~~~~~

To begin, navigate to https://www.arduino.cc/en/software.

Click ``Windows Win 10 and newer, 64 bits`` under the most recent version of IDE. This may be different than the screenshot below



When the page loads, click next





Installation
~~~~~~~~~~~~

To install Arduino IDE, navigate to where you saved your ``arduino-ide_2.x.x_Windows_64bit.exe`` file and follow the instructions in the install.

Software Configuration
======================

Board Manager
~~~~~~~~~~~~~

To properly configure IDE, the board manager for the XIAO RP2040 needs to be installed.

In Arduino IDE, navigate to **File > Preferences**. In the window, enter ``https://github.com/earlephilhower/arduino-pico/releases/download/global/package_rp2040_index.json`` into the **Additional boards manager URLs:** text box.



Click **OK**

Next, navigate to **Tools > Board: > Boards Manager...**. Search for ``Raspberry Pi Pico/RP2040`` and click **INSTALL** on the option published by Earle F. Philhower, III.



Code Libraries
~~~~~~~~~~~~~~

Several libraries are needed  to upload code to the weather station.

To install these libraries, navigate to **Tools > Manage Libraries...**

In the search box enter the following library names and install each including any required dependancies.

* ``Adafruit BME280 Library``
* ``Adafruit LTR390 Library``
* ``Adafruit SSD1306``
* ``Adafruit VEML7700 Library``
* ``ENS160 - Adafruit Fork``
* ``Sensirion I2C SCD4x``

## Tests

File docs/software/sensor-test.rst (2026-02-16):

.. Copyright 2026 Destination SPACE Inc.
   Licensed under the Apache License, Version 2.0 (the "License");
   you may not use this file except in compliance with the License.
   You may obtain a copy of the License at

      http://www.apache.org/licenses/LICENSE-2.0

   Unless required by applicable law or agreed to in writing, software
   distributed under the License is distributed on an "AS IS" BASIS,
   WITHOUT WARRANTIES OR CONDITIONS OF ANY KIND, either express or implied.
   See the License for the specific language governing permissions and
   limitations under the License.

.. _sensor-test:

Sensor Test Sketch
==================

The `Sensor Test <https://github.com/Destination-SPACE/DS-Weather-Station-V4_5/blob/main/software/Sensor_Test/Sensor_Test.ino>`_ sketch is used to make sure the sensors on the weather station are working correctly. Use this sketch as the first program to upload after the `Blink <https://github.com/Destination-SPACE/DS-Weather-Station-V4_5/blob/main/software/Blink/Blink.ino>`_ sketch.

Libraries
---------

For the Sensor Test sketch, many more libraries are required. These can be split into two categories; System libraries and sensor libraries. In this example only one system library is required, which is the `Wire Library <https://docs.arduino.cc/learn/communication/wire/#wire-library>`_. This is a default Arduino library and is used to communicate with sensors on the Inter-Integrated Circuit (I2C) protocol. More details about the protocol can be found `here <https://docs.arduino.cc/learn/communication/wire/>`_.

The libraries required to use all of the sensors on your weather stations and for the classroom expansion sensors have been pre-installed. A list of the libraries are below.

.. code-block:: cpp
   
   //Import system libraries
   #include <Wire.h>

   //Import sensor libraries
   #include <Adafruit_BME280.h>
   #include <Adafruit_LTR390.h>
   #include <Adafruit_Sensor.h>
   #include <Adafruit_VEML7700.h>
   #include <ScioSense_ENS160.h>
   #include <SensirionI2CScd4x.h>

Hardware Definitions
--------------------
Only one hardware definition is required for this example. This defines mean sea-level pressure, which is used to calculate an approximate value for altitude using temperature and pressure. By default, this value is set to 1013.25 hPa. You are welcome to change this value to the current sea-level pressure in your region. Click `here <>`_ to find out more about calculating barometric altitude.

.. code-block:: cpp
   
   #define SEALEVELPRESSURE_HPA (1013.25)

Define Sensor Functions
-----------------------

Several sensor functions need to be defined to get the sensors to work. This ensures that each sensor is communicating to the correct `address <https://learn.adafruit.com/i2c-addresses/overview>`_. These are also used to define which variable you will be using to communicate with the sensor.

.. code-block:: cpp

   Adafruit_BME280 BME280;
   Adafruit_LTR390 LTR390 = Adafruit_LTR390();
   Adafruit_VEML7700 VEML7700 = Adafruit_VEML7700();
   ScioSense_ENS160 ENS160(ENS160_I2CADDR_0);
   SensirionI2CScd4x scd4x;

Define Data Types
-----------------

The next step is to define the data types of each variable. A data type is a way to standardize the formatting of a variable, such as if it is a text value, integer, boolean (True/False), or number with decimal places. Click `here <https://en.cppreference.com/w/cpp/language/types>`_ for the definitions of C++ fundamental types.

Below you can find the data types of the variables used in this example program. The version in the final code file is condensed to save on line-count.

.. code-block:: cpp

   float BME280_TEMP;      // Temperature
   float BME280_PRES;      // Pressure
   float BME280_HUMD;      // Humidity
   float BME280_HI;        // Heat-index
   float BME280_ALT;       // Barometric altitude
   float ENS160_AQI;       // Air Quality Index
   float ENS160_AQI_PREV;  // Previous AQI value
   float ENS160_TVOC;      // Total Volatile Organic Compounds
   float ENS160_eCO2;      // Calculated CO2 concentration
   float LTR390_UVI;       // Ultra-Violet Index
   float LTR390_RAW;       // Raw UV data
   float VEML7700_ALS;     // Ambient light data
   float VEML7700_WHITE;   // How much of the incoming light is white
   float VEML7700_LUX;     // Ambient light intensity
   float SCD40_CO2;        // Measured CO2 concentration
   float SCD40_TEMP;       // Temperature data from the CO2 sensor
   float SCD40_HUMD;       // Humidity data from the CO2 sensor
   
   int clock_timer;        // Time between data recordings
   int hh;                 // hours elapsed
   int mm;                 // minutes elapsed
   int ss;                 // seconds elapsed

   uint16_t SCD40_CO2_RAW; // Raw CO2 data

Setup Function
---------------

The next section is for the setup function. This is where all of the sensors are initialized and confirmed if they are connected or not. Each sensor has a slightly different initialization process, which is determined by the sensor libraries. Essentially, each sensor is checked to see if it is attached; if it is not, then it's status indicator is set to 0/False. Lastly, a header for all of the data parameters is printed to the serial monitor.

.. code-block:: cpp

   void setup() {
      Serial.begin(115200); // Set serial stream to 115200bits/s
      while(!Serial); // Wait until serial monitor is open

      //Initialize BME280 sensor
      if(!BME280.begin(0x76, &Wire)){
         Serial.print("\n\nBME280 not found");
      }

      //Initialize ENS160 sensor
      if(ENS160.begin()){
         if(!ENS160.setMode(ENS160_OPMODE_STD)){
            Serial.print("\n\nENS160 failed to init");
            ENS160_STS = 0;
         }
         delay(10);
         if(ENS160.available()){
            ENS160.measure(true);
            ENS160_AQI_PREV = ENS160.getAQI();
         }
      }
      else{
         Serial.print("\n\nENS160 not found");
         ENS160_STS = 0;
      }

      //Initialize LTR390 sensor
      if(!LTR390.begin()){
         Serial.print("\n\nLTR390 not found");
         LTR390_STS = 0;
      }
      else{
         LTR390.setMode(LTR390_MODE_UVS);
         LTR390.setGain(LTR390_GAIN_3);
         LTR390.setResolution(LTR390_RESOLUTION_16BIT);
         LTR390.setThresholds(100,1000);
         LTR390.configInterrupt(true, LTR390_MODE_UVS);
      }

      //Initialize VEML7700 sensor
      if(!VEML7700.begin()){
         Serial.print("\n\nVEML7700 not found");
         VEML7700_STS = 0;
      }
      else{
         VEML7700.setLowThreshold(10000);
         VEML7700.setHighThreshold(20000);
         VEML7700.interruptEnable(true);
      }

      //Initialize SCD40 sensor
      scd4x.begin(Wire);
      if(scd4x.stopPeriodicMeasurement() || scd4x.startPeriodicMeasurement()){
            Serial.print("\n\nSCD40 failed to respond");
            SCD40_STS = 0;
      }
      //Print data table header
      Serial.print("\n\n+==============================================================================+\n|  TIME  | TEMP | HUM |  HI  | PRES | ALT | CO2 | TVOC |  AQI  |  UVI  |  LUX  |\n|hh:mm:ss| (°C) | (%) | (°C) | hPa  | (m) |(ppm)|(ppb.)|(0-300)|(0-+11)|(k-lux)|\n+==============================================================================+");
      
      //Set timer variables to zero
      clock_timer = 0;
      hh = 0;
      mm = 0;
      ss = 0;
   }

Loop Function
-------------

The loop function is the main portion of the software where the data is collected and displayed. First, the variable for the delay_timer is set to be equal to the current processor clock time (in milliseconds). This is to help the code make sure it is refreshing at the correct rate.

.. code-block:: cpp
   
   int delay_timer = millis();

The next step is to read from all the individual sensors and preform any relevant calculations. Again, each sensor has it's own method to collect data.

BME280
^^^^^^

The Adafruit library for the BME280 makes it simple to collect data. It is a simple read function where you define the target variable and assign the data value to it.

.. code-block:: cpp

   BME280_TEMP = BME280.readTemperature();
   BME280_PRES = BME280.readPressure() / 100.0F;
   BME280_HUMD = BME280.readHumidity();
   BME280_ALT = BME280.readAltitude(SEALEVELPRESSURE_HPA);

Now, the data can be interpreted to get the desired weather parameters. With the BME280 weather sensor several parameters can be calculated. The ones featured in this program are `dew point <https://en.wikipedia.org/wiki/Dew_point>`_, `absolute humidity <https://en.wikipedia.org/wiki/Humidity>`_, and `heat index <https://en.wikipedia.org/wiki/Heat_index>`_. Only the calculation for heat index is active by default, but you can uncomment the dew point and absolute humidity calculations to include them. 

Heat index is calculated using `dry-bulb temperature <https://en.wikipedia.org/wiki/Dry-bulb_temperature>`_ and relative humidity. The formula used to calculate heat index was first derived in `The Assessment of Sultriness. Part I: A Temperature-Humidity Index Based on Human Physiology and Clothing Science <https://journals.ametsoc.org/view/journals/apme/18/7/1520-0450_1979_018_0861_taospi_2_0_co_2.xml>`_ by R.G. Steadman in 1979. His results were then interpreted by the National Weather Service in technical report `SR 90-23 <https://www.weather.gov/media/ffc/ta_htindx.PDF>`_ in 1990 to be approximated into an equation.

.. math:: 
   :label: Heat-index equation
   :nowrap:

   \(HI = -42.379 + 2.04901523 \cdot T + 10.14333127 \cdot RH - 0.22375541 \cdot T \cdot RH - 6.83783 \cdot 10^(-3) \cdot T^2 - 5.481717 \cdot 10^(-2) \cdot RH^2 + 1.22874 \cdot 10^(-3) \cdot T^2 \cdot RH + 8.5282 \cdot 10 \cdot (-4) \cdot T \cdot RH^2 - 1.99 \cdot 10^(-6) \cdot T^2 \cdot RH^2\)

Where T is temperature in Fahrenheit and RH is relative humidity.

Because this is a regression fit, the equation has an error of ±1.3°F.

.. code-block:: cpp

   float h = (log10(BME280_HUMD)-2.0)/0.4343+(17.62*BME280_TEMP)/(243.12+BME280_TEMP);
  
   //Uncomment to calculate dew point and absolute humidity
   //float BME280_DEW_POINT = 243.12*h/(17.62-h); // Calculate dew point
   //float BME280_ABSOLUTE_HUMIDITY = 216.7*(BME280_HUMD/100.0*6.112*exp(17.62*BME280_TEMP/(243.12+BME280_TEMP))/(275.15+BME280_TEMP)); // Calculate absolute humidity

   float BME280_TEMP_F = (1.8*BME280_TEMP) + 32.0; // Convert Celsius to Fahrenheit

   //Calculate heat-index
   float BME280_HI_F = -42.379 + 2.04901523*BME280_TEMP_F + 10.14333127*BME280_HUMD - 0.22475541*BME280_TEMP_F*BME280_HUMD - 0.00683783*BME280_TEMP_F*BME280_TEMP_F - 0.05481717*BME280_HUMD*BME280_HUMD + 0.00122874*BME280_TEMP_F*BME280_TEMP_F*BME280_HUMD + 0.00085282*BME280_TEMP_F*BME280_HUMD*BME280_HUMD - 0.00000199*BME280_TEMP_F*BME280_TEMP_F*BME280_HUMD*BME280_HUMD; // Initial heat-index value

   if(BME280_HUMD < 13.0 && BME280_TEMP_F > 80.0 && BME280_TEMP_F < 112.0){ // If RH < 13% and 80 < T < 112
      BME280_HI_F = BME280_HI_F + (13.0 - BME280_HUMD)/4.0*sqrtf((17.0 - abs(BME280_TEMP_F - 95.0))/17);
   }
   else if(BME280_HUMD > 85 && BME280_TEMP_F > 80.0 && BME280_TEMP_F < 87.0){ // If RH > 85% and 80 < T < 87
      BME280_HI_F = BME280_HI_F + (BME280_HUMD - 85.0)/10*(87 - BME280_TEMP_F)/5;
   }
   else if(BME280_HI_F < 80.0){ // If HI < 80
      BME280_HI_F = 0.5 * (BME280_HI_F + 61.0 + 1.2*(BME280_HI_F - 68.0) + BME280_HUMD*0.094);
   }

   BME280_HI = (5.0/9.0)*(BME280_HI_F - 32.0); // Convert back to Celsius

ENS160
^^^^^^

The data collecting method for the ENS160 is very similar to the BME280. The parameters being collected are Air Quality Index (AQI) calculated from the German Federal Environmental Agency model, which is on a scale from 1 - 5, total volatile organic compounds (TVOC), and a calculated measurement of approximate Carbon-Dioxide concentration (eCO2).

.. code-block:: cpp

   ENS160.measure(true);
   ENS160_AQI = ENS160.getAQI();
   ENS160_TVOC = ENS160.getTVOC();
   ENS160_eCO2 = ENS160.geteCO2();

No further calculations need to be completed for this sensor.

LTR390
^^^^^^

Just like before, only the data needs to be pulled from the sensor with minimal calculations.

.. code-block:: cpp

   LTR390_RAW = LTR390.readUVS();
   LTR390_UVI = LTR390_RAW / 2300.00;

VEML7700
^^^^^^^^

.. code-block:: cpp

   VEML7700_LUX = VEML7700.readLux();

SCD40
^^^^^

.. code-block:: cpp

   bool isDataReady = false; // Reset Data-Ready flag
   if(scd4x.getDataReadyFlag(isDataReady)){
   }

   if(isDataReady){
      if(scd4x.readMeasurement(SCD40_CO2_RAW, SCD40_TEMP, SCD40_HUMD)){
      }
      else if(SCD40_CO2_RAW == 0){
      } 
      else{
         SCD40_CO2 = static_cast<float>(SCD40_CO2_RAW);
      }
   }
   else{
   }

Full Code
--------- 

Below is the full Sensor Test example sketch

.. code-block:: cpp

   //Import system libraries
   #include <Wire.h>

   //Import sensor libraries
   #include <Adafruit_BME280.h>
   #include <Adafruit_LTR390.h>
   #include <Adafruit_Sensor.h>
   #include <Adafruit_VEML7700.h>
   #include <ScioSense_ENS160.h>
   #include <SensirionI2CScd4x.h>

   #define SEALEVELPRESSURE_HPA (1013.25) //Define sea-level pressure as 1013.25hPa

   //Set sensor functions
   Adafruit_BME280 BME280;
   Adafruit_LTR390 LTR390 = Adafruit_LTR390();
   Adafruit_VEML7700 VEML7700 = Adafruit_VEML7700();
   ScioSense_ENS160 ENS160(ENS160_I2CADDR_0);
   SensirionI2CScd4x scd4x;

   //Define data types
   float BME280_TEMP, BME280_PRES, BME280_HUMD, BME280_HI, BME280_ALT, ENS160_AQI, ENS160_AQI_PREV, ENS160_TVOC, ENS160_eCO2, LTR390_UVI, LTR390_RAW, VEML7700_ALS, VEML7700_WHITE, VEML7700_LUX, SCD40_CO2, SCD40_TEMP, SCD40_HUMD;
   bool ENS160_STS = 1;
   bool LTR390_STS = 1;
   bool VEML7700_STS = 1;
   bool SCD40_STS = 1;
   int clock_timer, hh, mm, ss;
   uint16_t SCD40_CO2_RAW;

   float TVOC_CONCENTRATION_MIN = 5000;
   float TVOC_CONCENTRATION_MAX = 0;

   void setup() {
   Serial.begin(115200); // Set serial stream to 115200bits/s
   while(!Serial); // Wait until serial monitor is open

   //Initialize BME280 sensor
   if(!BME280.begin(0x76, &Wire)){
      Serial.print("\n\nBME280 not found");
   }

   //Initialize ENS160 sensor
   if(ENS160.begin()){
      if(!ENS160.setMode(ENS160_OPMODE_STD)){
         Serial.print("\n\nENS160 failed to init");
         ENS160_STS = 0;
      }
      delay(10);
      if(ENS160.available()){
         ENS160.measure(true);
         ENS160_AQI_PREV = ENS160.getAQI();
      }
   }
   else{
      Serial.print("\n\nENS160 not found");
      ENS160_STS = 0;
   }

   //Initialize LTR390 sensor
   if(!LTR390.begin()){
      Serial.print("\n\nLTR390 not found");
      LTR390_STS = 0;
   }
   else{
      LTR390.setMode(LTR390_MODE_UVS);
      LTR390.setGain(LTR390_GAIN_3);
      LTR390.setResolution(LTR390_RESOLUTION_16BIT);
      LTR390.setThresholds(100,1000);
      LTR390.configInterrupt(true, LTR390_MODE_UVS);
   }

   //Initialize VEML7700 sensor
   if(!VEML7700.begin()){
      Serial.print("\n\nVEML7700 not found");
      VEML7700_STS = 0;
   }
   else{
      VEML7700.setLowThreshold(10000);
      VEML7700.setHighThreshold(20000);
      VEML7700.interruptEnable(true);
   }

   //Initialize SCD40 sensor
   scd4x.begin(Wire);
   if(scd4x.stopPeriodicMeasurement() || scd4x.startPeriodicMeasurement()){
         Serial.print("\n\nSCD40 failed to respond");
         SCD40_STS = 0;
   }

   //Print data table header
   Serial.print("\n\n+==============================================================================+\n|  TIME  | TEMP | HUM |  HI  | PRES | ALT | CO2 | TVOC |  AQI  |  UVI  |  LUX  |\n|hh:mm:ss| (°C) | (%) | (°C) | hPa  | (m) |(ppm)|(ppb.)| (1-5) |(0-+11)|(k-lux)|\n+==============================================================================+");
   
   //Set timer variables to zero
   clock_timer = 0;
   hh = 0;
   mm = 0;
   ss = 0;
   }

   void loop() {
   int delay_timer = millis(); // Reset delay timer

   //Collect Data from BME280
   BME280_TEMP = BME280.readTemperature();
   BME280_PRES = BME280.readPressure() / 100.0F;
   BME280_HUMD = BME280.readHumidity();
   BME280_ALT = BME280.readAltitude(SEALEVELPRESSURE_HPA);

   float h = (log10(BME280_HUMD)-2.0)/0.4343+(17.62*BME280_TEMP)/(243.12+BME280_TEMP);
   
   //Uncomment to calculate dew point and absolute humidity
   //float BME280_DEW_POINT = 243.12*h/(17.62-h); // Calculate dew point
   //float BME280_ABSOLUTE_HUMIDITY = 216.7*(BME280_HUMD/100.0*6.112*exp(17.62*BME280_TEMP/(243.12+BME280_TEMP))/(275.15+BME280_TEMP)); // Calculate absolute humidity

   float BME280_TEMP_F = (1.8*BME280_TEMP) + 32.0; // Convert Celsius to Fahrenheit

   //Calculate heat-index
   float BME280_HI_F = -42.379 + 2.04901523*BME280_TEMP_F + 10.14333127*BME280_HUMD - 0.22475541*BME280_TEMP_F*BME280_HUMD - 0.00683783*BME280_TEMP_F*BME280_TEMP_F - 0.05481717*BME280_HUMD*BME280_HUMD + 0.00122874*BME280_TEMP_F*BME280_TEMP_F*BME280_HUMD + 0.00085282*BME280_TEMP_F*BME280_HUMD*BME280_HUMD - 0.00000199*BME280_TEMP_F*BME280_TEMP_F*BME280_HUMD*BME280_HUMD; // Initial heat-index value

   if(BME280_HUMD < 13.0 && BME280_TEMP_F > 80.0 && BME280_TEMP_F < 112.0){ // If RH < 13% and 80 < T < 112
      BME280_HI_F = BME280_HI_F + (13.0 - BME280_HUMD)/4.0*sqrtf((17.0 - abs(BME280_TEMP_F - 95.0))/17);
   }
   else if(BME280_HUMD > 85 && BME280_TEMP_F > 80.0 && BME280_TEMP_F < 87.0){ // If RH > 85% and 80 < T < 87
      BME280_HI_F = BME280_HI_F + (BME280_HUMD - 85.0)/10*(87 - BME280_TEMP_F)/5;
   }
   else if(BME280_HI_F < 80.0){ // If HI < 80
      BME280_HI_F = 0.5 * (BME280_HI_F + 61.0 + 1.2*(BME280_HI_F - 68.0) + BME280_HUMD*0.094);
   }

   BME280_HI = (5.0/9.0)*(BME280_HI_F - 32.0); // Convert back to Celsius
   
   // Retrieve data from ENS160 VOC sensor
   if(ENS160_STS && ENS160.available()){
      ENS160.measure(true);
      ENS160_AQI = ENS160.getAQI(); // Get air quality index
      ENS160_TVOC = ENS160.getTVOC(); // Get total volatile organic compound concentration in parts per billion
      ENS160_eCO2 = ENS160.geteCO2(); // Get eCO2 measurement, derived from TVOC
   }
   else{
      ENS160_AQI = 0;
      ENS160_TVOC = 0;
      ENS160_eCO2 = 0;
   }

   //Retrieve data from LTR390 UVA sensor
   if(LTR390_STS && LTR390.newDataAvailable()){
      LTR390_RAW = LTR390.readUVS();
      LTR390_UVI = LTR390_RAW / 2300.00; // Calculate UV-index from raw values
   }
   else{
      LTR390_UVI = 0;
   }

   if(VEML7700_STS){
      VEML7700_LUX = VEML7700.readLux(); // Retrieve data from VEML7700 ALS sensor
   }
   else{
      VEML7700_LUX = 0;
   }

   //Retrieve data from SCD40 CO2 sensors
   if(SCD40_STS){
      bool isDataReady = false; // Reset Data-Ready flag
      if(scd4x.getDataReadyFlag(isDataReady)){ // Check if there is data available to read
      }

      if(isDataReady){ // If data is ready to be read, read data
         if(scd4x.readMeasurement(SCD40_CO2_RAW, SCD40_TEMP, SCD40_HUMD)){
         }
         else if(SCD40_CO2_RAW == 0){ // If CO2 data is zero, keep data
         } 
         else{
            SCD40_CO2 = static_cast<float>(SCD40_CO2_RAW); // Cast CO2 unsigned 16bit-integer to type float
         }
      }
      else{ // If data is not ready, skip measurement
      }
   }
   else{
      SCD40_CO2 = 0;
   }
   
   //Clock timer
   ss = (millis() - clock_timer)/1000; // Set seconds to how much time has elapsed since first data read
   if(ss >= 60){ // If seconds is 60+, add 1 minutes and reset seconds variable
      clock_timer = millis();
      ss = ss - 60;
      mm = mm + 1;
      if(mm >= 60){ // If minutes is 60+, add 1 hours and reset minutes and seconds
         ss = ss - 60;
         mm = mm - 60;
         hh = hh + 1;
      }
   }

   char buffer[1024]; // Create 1024-bit buffer for data output
   sprintf(buffer, "\n|%02d:%02d:%02d| %5.2f|%5.2f| %5.2f|%6.1f|%5.1f| %4.0f| %5.0f|  %5.0f|  %5.2f|%7.2f|", hh, mm, ss, BME280_TEMP, BME280_HUMD, BME280_HI, BME280_PRES, BME280_ALT, SCD40_CO2, ENS160_TVOC, ENS160_AQI, LTR390_UVI, VEML7700_LUX);
   Serial.print(buffer); // Print buffer
   
   //Idle until it is time for next data read
   while(true){
      if(millis() - delay_timer >= 1000) break;
      delay(5);
      }
   }
0.

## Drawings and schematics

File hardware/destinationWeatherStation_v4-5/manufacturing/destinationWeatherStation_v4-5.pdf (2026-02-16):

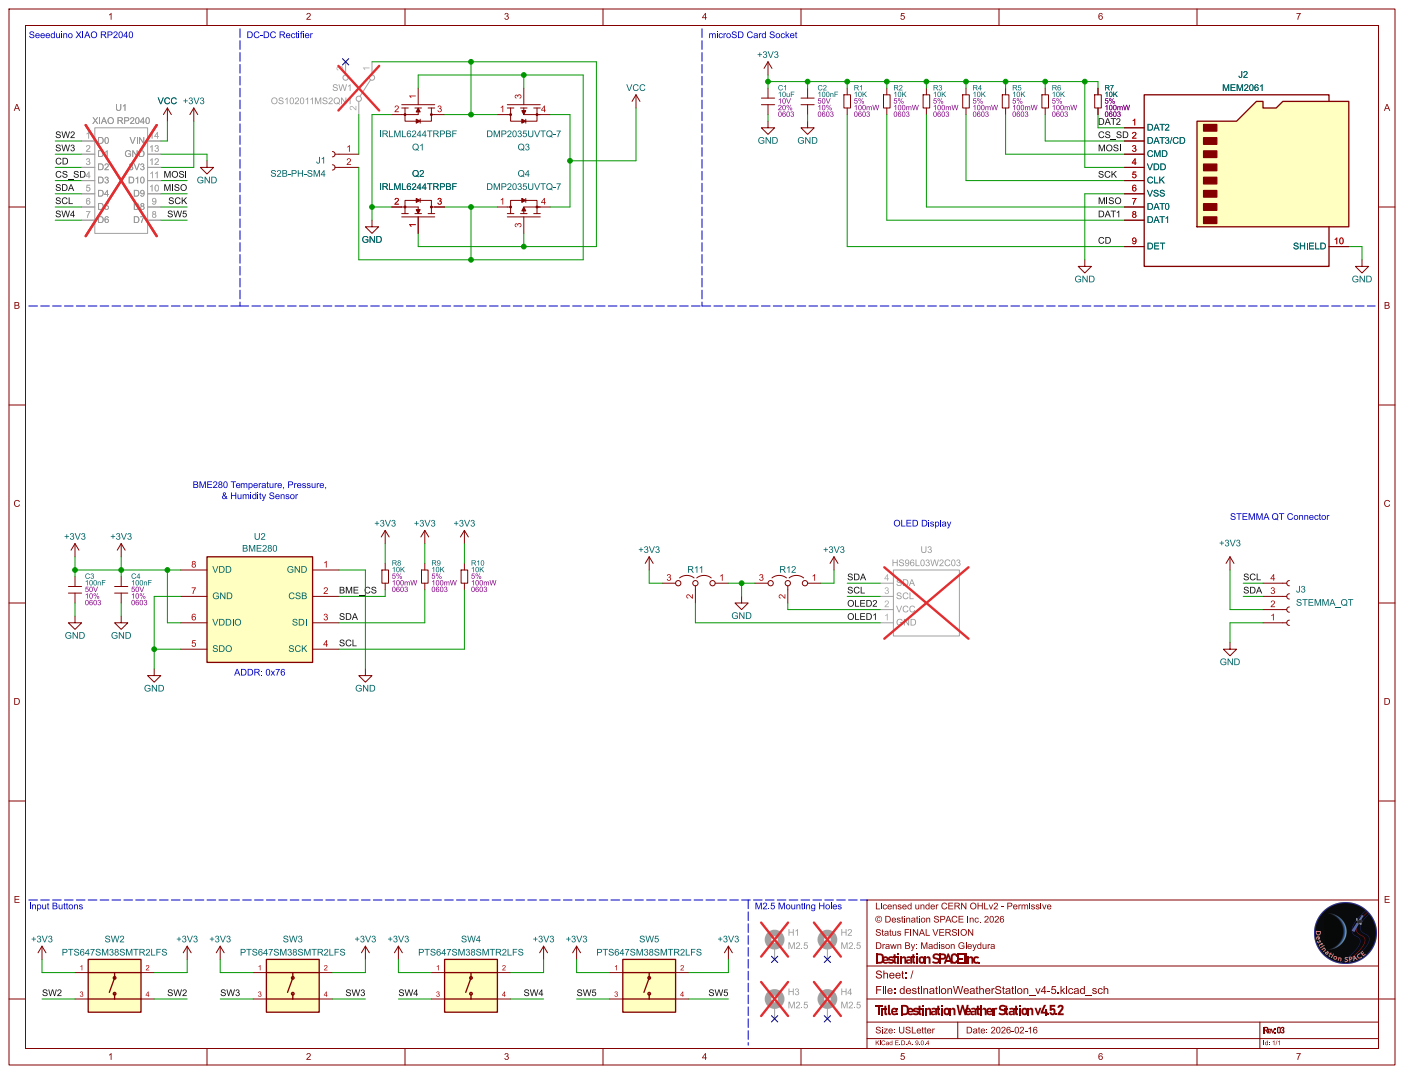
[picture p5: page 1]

Licensed under CERN OHLv2 - Permissive +3V3 GND

þÿ©Destination SPACE Inc. 2026
Destination SPACEInc. Drawn By: Madison Gleydura Status FINAL VERSION

Sheet: /
File: destinationWeatherStation_v4-5.kicad_sch
Id: 1/1 Title:Destination Weather Stationv4.5.2

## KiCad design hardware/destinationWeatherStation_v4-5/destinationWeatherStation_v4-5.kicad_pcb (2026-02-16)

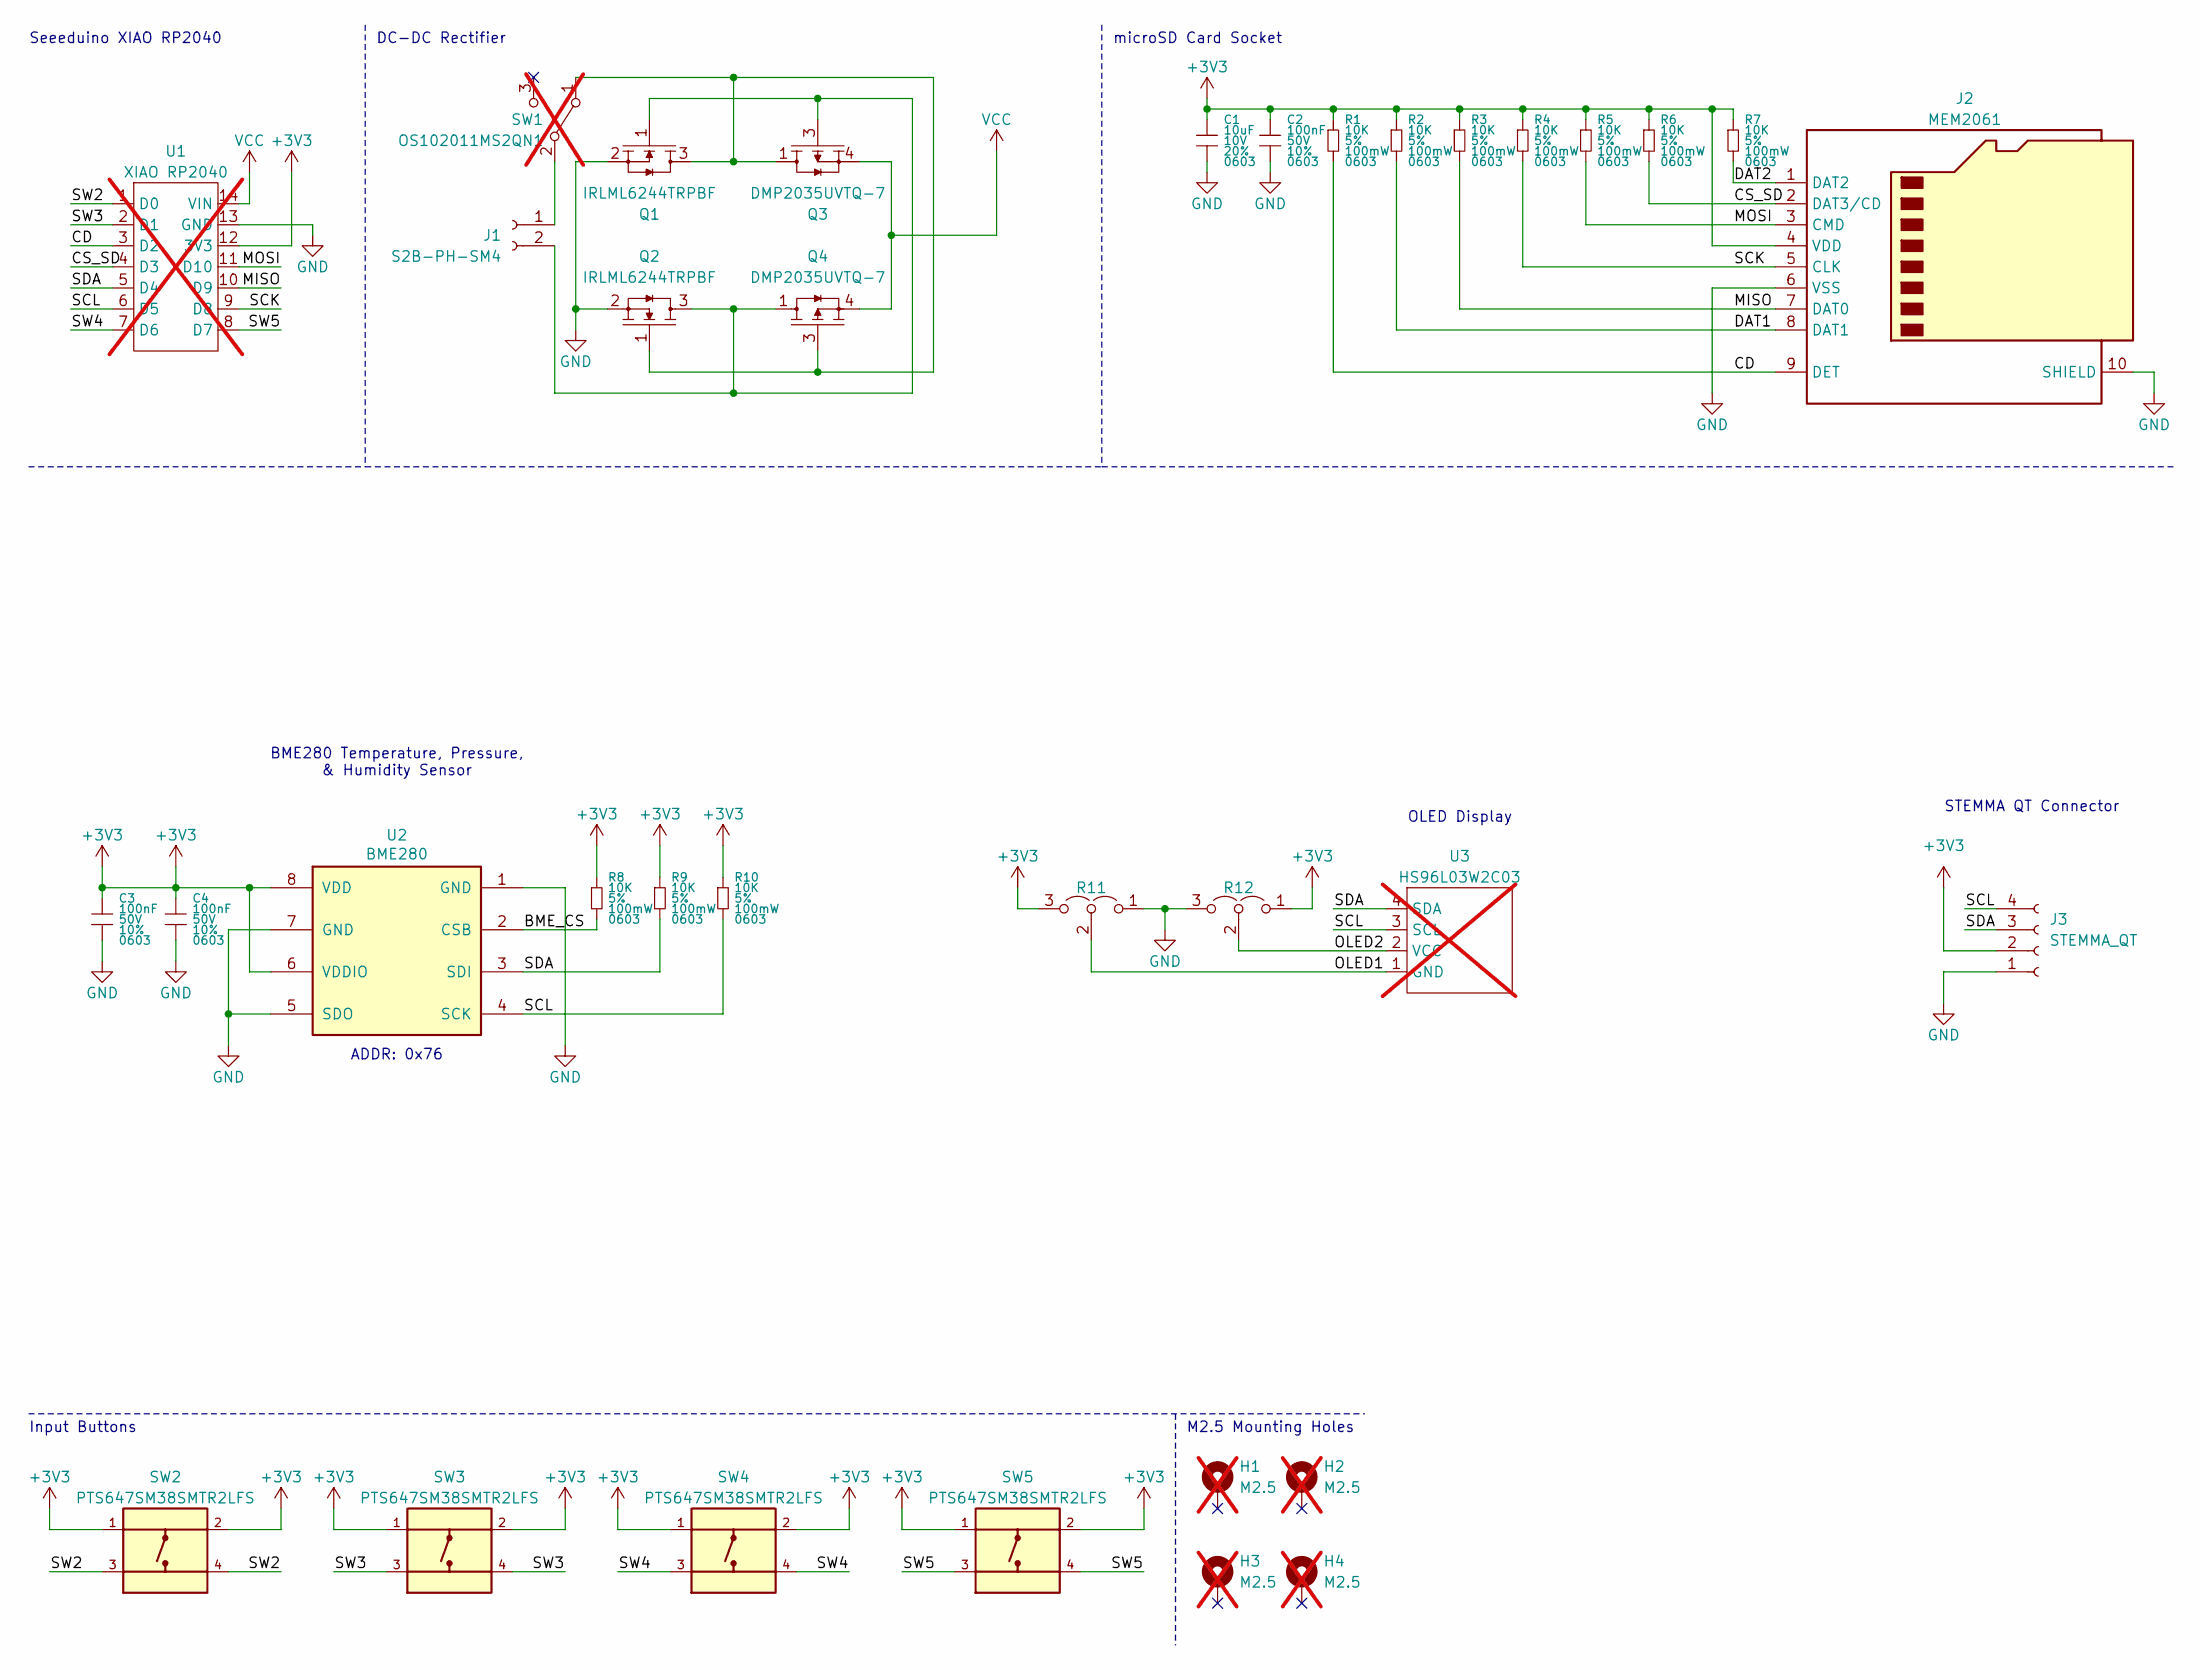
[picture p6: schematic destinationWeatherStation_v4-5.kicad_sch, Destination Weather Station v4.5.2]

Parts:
C1: 10uF; CAPC160X80X88L35N; Tolerance 20%; Voltage Rating 10V; MPN KGM15CR51A106MT; JLCPCB PN C1691
C2, C3, C4: 100nF; CAPC160X80X88L35N; Tolerance 10%; Voltage Rating 50V; MPN KGM15AR51H104KT; JLCPCB PN C1590
H1, H2, H3, H4: M2.5; M2.54_NPTH; not fitted
J1: S2B-PH-SM4; JST-PH-S2B-SM4-TB; MPN S2B-PH-SM4-TB(LF)(SN); JLCPCB PN C295747
J2: MEM2061; MPN MEM2061-01-188-00-A; JLCPCB PN C5151738
J3: STEMMA_QT; JST_SH_SM04B-SRSS-TB; MPN SM04B-SRSS-TB; JLCPCB PN C160404
Q1, Q2: IRLML6244TRPBF; MPN IRLML6244TRPBF; JLCPCB PN C5123965
Q3, Q4: DMP2035UVTQ-7; SOT23-6P95_280X100L40X37N; MPN DMP2035UVTQ-7; JLCPCB PN C5126680
R1, R2, R3, R4, R5, R6, R7, R8, R9, R10: 10K; RESC160X80X55L30N; Tolerance 5%; Power Rating 100mW; MPN CRCW060310K0JNEB; JLCPCB PN C1511834
R11, R12: 0R; ResistorJumper-3; MPN CRCW06030000Z0EA; JLCPCB PN C844915
SW1: OS102011MS2QN1; MPN OS102011MS2QN1; JLCPCB PN C221829; not fitted
SW2, SW3, SW4, SW5: PTS647SM38SMTR2LFS; SW_4.5x4.5; MPN PTS 647 SM38 SMTR2 LFS; JLCPCB PN C2689502
U1: XIAO RP2040; QtPy; MPN RP2040; JLCPCB PN N/A; not fitted
U2: BME280; MPN BME280; JLCPCB PN C92489
U3: HS96L03W2C03; MPN HS96L03W2C03; JLCPCB PN C5248080; not fitted

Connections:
+3V3: C1.1, C2.1, C3.1, C4.1, J2.4 (VDD), J3.2, R1.1, R2.1, R3.1, R4.1, R5.1, R6.1, R7.1, R8.1, R9.1, R10.1, R11.3 (B), R12.1 (A), SW2.1, SW2.2, SW3.1, SW3.2, SW4.1, SW4.2, SW5.1, SW5.2, U1.12 (3V3), U2.6 (VDDIO), U2.8 (VDD)
/BME_CS: R8.2, U2.2 (CSB)
/CD: J2.9 (DET), R1.2, U1.3 (D2)
/CS_SD: J2.2 (DAT3/CD), R6.2, U1.4 (D3)
/DAT1: J2.8 (DAT1), R2.2
/DAT2: J2.1 (DAT2), R7.2
/MISO: J2.7 (DAT0), R3.2, U1.10 (D9)
/MOSI: J2.3 (CMD), R5.2, U1.11 (D10)
/OLED1: R11.2 (C), U3.1 (GND)
/OLED2: R12.2 (C), U3.2 (VCC)
/SCK: J2.5 (CLK), R4.2, U1.9 (D8)
/SCL: J3.4, R10.2, U1.6 (D5), U2.4 (SCK), U3.3 (SCL)
/SDA: J3.3, R9.2, U1.5 (D4), U2.3 (SDI), U3.4 (SDA)
/SW2: SW2.3, SW2.4, U1.1 (D0)
/SW3: SW3.3, SW3.4, U1.2 (D1)
/SW4: SW4.3, SW4.4, U1.7 (D6)
/SW5: SW5.3, SW5.4, U1.8 (D7)
GND: C1.2, C2.2, C3.2, C4.2, J2.6 (VSS), J2.10 (SHIELD), J3.1, Q1.2, Q2.2, R11.1 (A), R12.3 (B), U1.13 (GND), U2.1 (GND), U2.5 (SDO), U2.7 (GND)
unnamed: J1.1, SW1.2 (B)
unnamed: J1.2, Q1.1, Q2.3, Q3.3, Q4.1, Q4.2, Q4.5, Q4.6
unnamed: Q1.3, Q2.1, Q3.1, Q3.2, Q3.5, Q3.6, Q4.3, SW1.1 (A)
VCC: Q3.4, Q4.4, U1.14 (VIN)

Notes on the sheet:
DC-DC Rectifier
ADDR: 0x76
OLED Display
Seeeduino XIAO RP2040
M2.5 Mounting Holes
Input Buttons
microSD Card Socket
STEMMA QT Connector
BME280 Temperature, Pressure, & Humidity Sensor

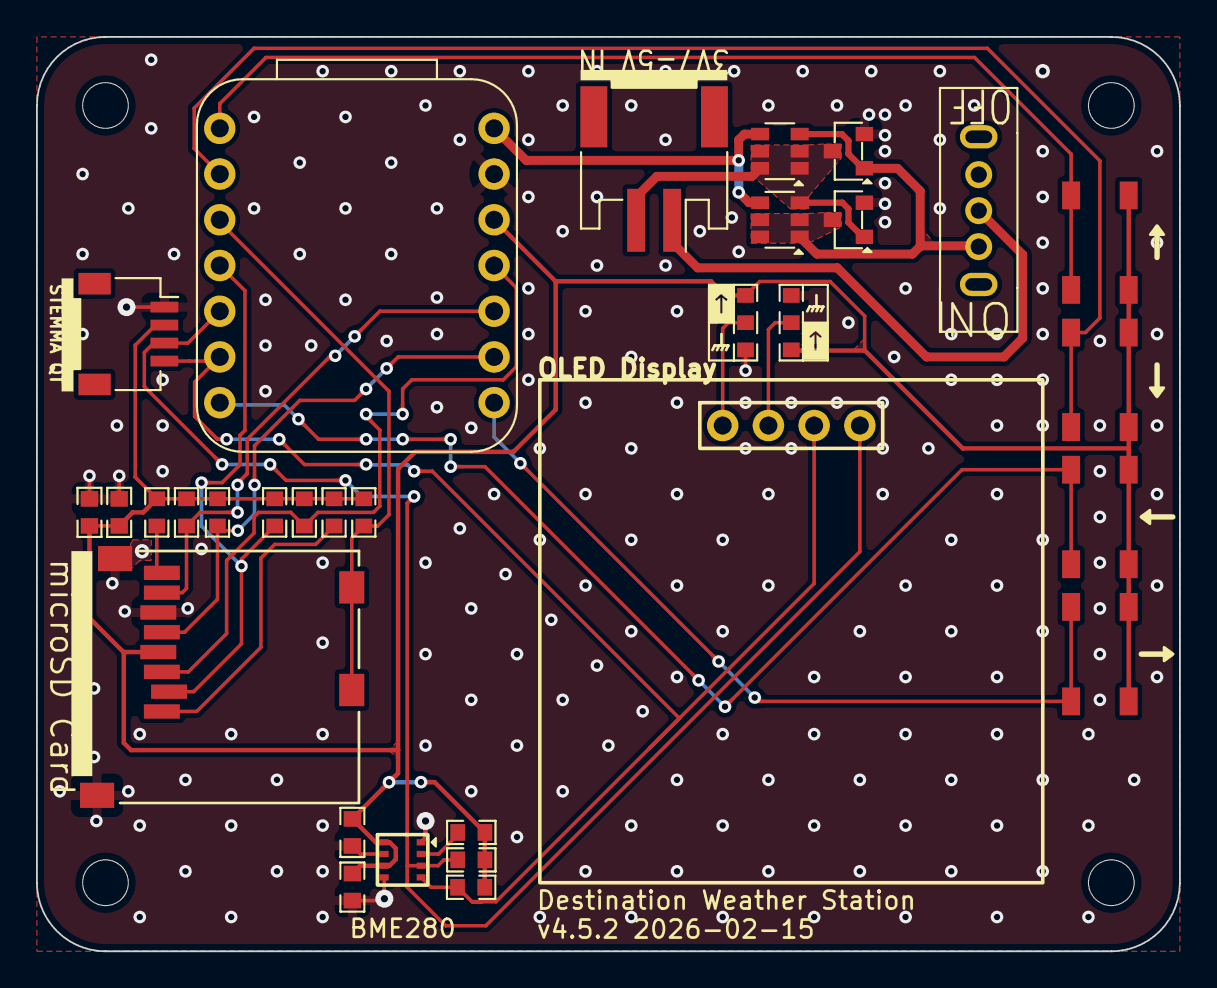
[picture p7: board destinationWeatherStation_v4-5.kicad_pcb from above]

Board: 2 copper layers, 63.5 x 50.8 mm, 35 parts (0 on the bottom side), 22 nets.

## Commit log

2026-01-30 fixing for final version
    [SS12D07VG4.STEP, destinationWeatherStation_v4-5.kicad_pcb, destinationWeatherStation_v4-5.kicad_sch]
2026-02-02 exported new gerbers
    [destinationWeatherStation_v4-5-B_Cu.gbr, destinationWeatherStation_v4-5-B_Fab.gbr, destinationWeatherStation_v4-5-B_Mask.gbr, destinationWeatherStation_v4-5-B_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]
2026-02-02 fixed schematic and linked datasheets
    [destinationWeatherStation_v4-5.kicad_sch]
2026-02-02 nudged traces and relinked footprints and models
    [destinationWeatherStation_v4-5.kicad_pcb]
2026-02-10 moved gerbers
    [destinationWeatherStation_v4-5-B_Cu.gbr, destinationWeatherStation_v4-5-B_Fab.gbr, destinationWeatherStation_v4-5-B_Mask.gbr, destinationWeatherStation_v4-5-B_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]
2026-02-10 moved BOM
    [bom.csv]
2026-02-10 manufacturing files
    [cpl.csv]
2026-02-15 re-exported gerbers
    [destinationWeatherStation_v4-5-B_Cu.gbr, destinationWeatherStation_v4-5-B_Fab.gbr, destinationWeatherStation_v4-5-B_Mask.gbr, destinationWeatherStation_v4-5-B_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]
2026-02-15 moved JLCPCB manufacturing files to subfolder
    [jlcpcb_bom.csv, jlcpcb_cpl.csv]
2026-02-15 updated silkscreen and fixed copper pours
    [destinationWeatherStation_v4-5.kicad_pcb]
2026-02-15 fixed dimension
    [destinationWeatherStation_v4-5.kicad_pcb]
2026-02-16 fixed R11 and R12 placement
    [jlcpcb_cpl.csv]
2026-02-16 fixed resistor placement
    [destinationWeatherStation_v4-5.kicad_pcb, destinationWeatherStation_v4-5.kicad_sch]
2026-02-16 exported schematics
    [destinationWeatherStation_v4-5.kicad_pcb, destinationWeatherStation_v4-5.kicad_sch]
